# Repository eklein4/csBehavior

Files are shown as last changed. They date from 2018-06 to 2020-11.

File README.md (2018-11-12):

# csBehavior

Tools for running behavioral experiments with Python and Teensy (and related) microcontrollers.

Example Features and Other Capabilities:
State based behavior control.
Runs reliably at 1 KHz.
Visual stimuli and camera tracking via an optional raspberry pi.
Multi-color optical stimulus control.
Event-driven clocking of analog outputs (tying optical stimulus to galvo turnarounds).
Electronic record keeping via mqtt and google sheets.

v1.05 (highly functional and precise, but not totally polished) 
<br>
questions: cdeister@brown.edu
</br>
<br>
contributors: Chris Deister, Sinda Fekir
</br>

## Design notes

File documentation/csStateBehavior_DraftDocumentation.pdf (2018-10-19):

csStateBehavior Documentation (9/22/2018)

About:
“csStateBheavior” is a micro-controller program for running state-based behavioral tasks and/or stimulus delivery.

Dependencies:
csStateBehavior uses some 3rd party libraries. Becuause the program is embedded, you need these libraries to compile and upload the code to a Teensy, even if you aren’t going to use the features they offer. You can install libraries into the Arduino IDE in a variety of ways, but I recommend downloading these libraries, placing them in a .zip and installing them by selecting “Sketch -> Include Library -> Add .zip library”
A) Adafruit’s neopixel library:
https://github.com/adafruit/Adafruit_NeoPixelhttps://github.com/adafruit/Adafruit_NeoPixel/archive/master.zip
This is used to control neopixel strips. Intended use is to have neopixel strips like this: https://www.adafruit.com/product/2847 or any of them, in a behavior rig enabling you to change light colors for cues, habituation reasons, or just to have light around.
B) HX711 ADC Library by Bodge:
https://github.com/bogde/HX711
https://github.com/bogde/HX711/archive/master.zip
This is to interface with and read data from the loadcell. There are a ton of HX711 libraries around, but Bodge got all the “little things” right.
C) Adafruit’s MCP4725 (DAC) Library
https://github.com/adafruit/Adafruit_MCP4725https://github.com/adafruit/Adafruit_MCP4725/archive/master.zip
There are a bunch of MCP libraries around too. This one is fine, and I like Adafruit. This is used to add two more DAC channels via MCP4725 breakouts. I use one from Adafruit and one from Sparkfun, because the default addresses differ. But, you can change the address of either and just buy two from one place. https://www.adafruit.com/product/935

Basics:
By default, csStateBehavior runs at 1 kHz. The program is a state machine instantiated as a function that is timed using and interrupt timer. Each interrupt a function called vStates runs and it:
a) evaluates which state it should be in
b) runs a state header if it enters a new state
c) executes code determined by its state
d) streams, over serial, a data report
e) interacts with experimental devices, with precise timing, via digital, analog, i2c, spi, or UART IO.

It is important to note that the intended approach of the broader csBehavior library to stimulus and behavior control involves using a python program to interact with the teensy, such that real-time processes are effected by the Teensy and the python program saves data, shows plots, and makes determinations about when to change states. In this way, the Teensy program is designed to be as “dumb” as possible, yet it is the core of the behavioral control stack. csStateBehavior provides the master clock, and the state the Teensy is in, is considered by all other interacting processes (like the python program) to be “ground truth.” Programs can request state changes, but the teensy changes the state and provides feedback when it has.

csStateBehavior, by default, sits in “State 0; S0” where it does very little. There is no data report sent in S0. However, in S0, the Teensy does evaluate whether it should move to a new state, responds to serial-based commands, and it can execute a series of pre-programmed device interactions “relays” based on specific relay pins being turned high. These relays are intended to allow other users the ability to gain access to devices attached to your Teensy/Behavior Rig without having to use the program or worry about weird current/voltage states on the dedicated trigger pins. For example, a user may be using Matlab code and NI-

DAQ boards to do their work, but they want to trigger a microscope, change light brightness, and trigger rewards from a pump. Instead of having to split connections, which can lead to unexpected behaviors, the user can trigger a pin on the Teensy and it will do any, or all, of those things. Also, in S0, the state of connected devices can be polled asynchronously for general use. For example, you can change the color of neopixel light strips, play tones, and check the values of attached sensors and devices. Lastly, certain sensors that cannot be polled in real-time can be used in S0 (such as environmental sensors).

Data Report:
What is streamed in the data report changes frequently, and can be customized. As of this writing, the data report streams the following in a serial packet that has a header called “tData:”
a) intCount: this is the actual number of interrupts fired since the Teensy has left S0. By default, csStateBehavior runs a 1kHz, thus, each interrupt is 1 ms. This should be considered to be the actual clock.
b) sesTime: this is the session clock, as determined by evaluating elapsedMillis(). Conceptually, this value should be identical to intCount. It can differ by 1 at the beginning, as sometimes the first ellapsedMillis will report 0 or 1. Beyond that, the two clocks should be identical. If it isn’t, that means the function did not finish evaluating before the next interrupt. Despite common conception, Teensy’s and related boards are very fast, each evaluation of vStates() takes less than 200 us.
c) stateTime: this is the state clock, as determined by evaluating elapsedMillis(), and resetting the reference each time you enter a new state. The intention of this variable is to help make evaluation of state-specific conditions/functions easier. Also, it may help with post-hoc analysis.
d) currentTeensyState (aka knownValues[0]): this is the current state the Teensy is in.
e) loadCellValue (aka knownValues[17]): this is the reading of the loadCell from the HX711 amplifier.
f) lickSensorA_Value: this is the value of the sensor used for determining licks. By default, even digital sensors are treated as analog allowing an external program to threshold as you see fit. csStateBehavior (the hardware) does not evaluate licks in real-time, and does not need to. Though, it is trivial to configure csStateBehavior to do hardware lick detection.
g) encoderAngle: this is the value reported by a rotary encoder used to track the location of a wheel.
h) pulseCountA: this is the incremental pulse count determined by an interrupt-based pulse counter. It can be used to keep track of elapsed frames from a two-photon microscope or ccd camera, etc. It resets every session.
i) loopTime: this is the amount of time in micro-seconds that the function took to evaluate for the last interrupt. The default clock rate of csStateBehavior is 1kHz, meaning that the interrupt timing the state machine function fires every ms, no exception. However, if the function does not return within a ms, you will fail to log those interrupts. Loop time allows you to identify problematic interrupts and fix any issue that may be slowing down the program. As configured, each loop of the main function takes 500-720 microseconds, depending on details of how it was compiled, primarily.

j-m) genAnalogInput0-3: these are the values of 4 different analog inputs chosen by the user. Just add your device to these and it will record the value. Note that the teensy is an arm-based computer and operates at 3.3V, the analog input has to be between 0 and 3.3V, not only to be precise, but the pins will become damaged if you drive them above 3.3V. Use a voltage divider to scale the peak voltage to 3.3V if you have something you know to exceed that voltage.

Generic State:
The generic state consists of the following:
A) State Header: code that only runs when you enter the state.
B) State Body: code that loops until you leave the state.

Every state runs the default state header and body. You can override these, and you can supplement them (prefered).

Anatomy of the default header:
The concept of “the header” is code you want to run only once and specifically when you arrive to the state. The obvious use of this is to reset a timer. Here is what the default header looks like:

void genericHeader(int stateNum) {
// a: reset header timer
headerTime = 0;
// b: reset header states and set current state's header to 1 (fired). resetHeaders();
headerStates[stateNum] = 1;
// c: set analog output values to 0.
analogOutVals[0] = 0;
analogOutVals[1] = 0;
analogOutVals[2] = 0;
analogOutVals[3] = 0;
// d: reset state timer.
stateTime = 0;
}

What this does is to reset a header timer, resets the state of all other state’s headers to 0 (hasn’t fired) while also setting the current state’s header to 1 (has fired), then it zeros out the analog output voltages ensuring that if you entered the state in the middle of a stimulus, it doesn’t hang, and lastly it resets the state timer.

The concept of the state timer (stateTime) is most important in creating your own states. Typically, you will want to do things based on how long you have been in a state. You can program hardware specific logic, but I recommend using the python component to react to time events etc. I mention this here because this variable (stateTime) is streamed over to python.

Anatomy of the default state body:

void genericStateBody() {
lickSensorAValue = analogRead(lickPinA); lickSensorAValue = analogRead(lickPinB); genAnalogInput0 = analogRead(genA0); genAnalogInput1 = analogRead(genA1); genAnalogInput2 = analogRead(genA2); genAnalogInput3 = analogRead(genA3); analogAngle = analogRead(analogMotion); writeAnalogOutValues(analogOutVals);
If (scale.is_ready()) {
scaleVal = scale.get_units() * 22000;
// this scale factor gives hundreths of a gram as the least significant int knownValues[14] = scaleVal;
}
}
What this does is, reads the values of up to two connected lick/touch sensors, the four generic analog inputs, an analog encoder, writes the currently desired/computed analog out voltages (see below) on the analog output channels, then it looks to see if load cell data is available, if so it grabs it and scales it to give useable numbers.

You can add specific code to the header or body in your custom state. Here is an example state:

// ************************** // State 1: Boot/Init State // **************************
if (knownValues[0] == 1) {

if (headerStates[1] == 0) { visStim(0);
genericHeader(1);
blockStateChange = 0;
}
genericStateBody();
}

From the top, this state is entered if the state variable (knownValues[0]) is 1. If it enters the first time (as indicated by it’s header bit being 0) it will zero out a visual stimulus (added code), run the default header, and will allow python to control the state (blockStateChange = 0). After this, the header bit will be set to 1 (which happens in the default header) then, it can’t run anymore as long as the program is stuck in state 1. But, instead, it will always fire “genericStateBody()” that is the default state body. If I wanted to add some code that changed the state after 100 ms, I could add the following:

// ************************** // State 1: Boot/Init State // **************************
if (knownValues[0] == 1) {

if (headerStates[1] == 0) { visStim(0);
genericHeader(1);
blockStateChange = 0;
}
genericStateBody();
if (stateTime >= 100){
// note that stateTime is in milliseconds knownValues[0] = 2;
// send teensy to state 2
}
}

But, as you will see in later parts of the documentation, it is recommended you handle such things in python. However, the more event logic you program on the teensy, the more close to true real-time performance you will get. The above code will move the teensy to state 2, in real-time, once 100 ms has elapsed, but if you are coordinating with the python component, it will need to be made aware.

There are two basic approaches to two components interacting dynamically, one is to have all events on the hardware, and stream the data for logging in software. Or, one can have the software log data, and determine state flow. The csBehavior library biases things towards software control in order to take advantage of richer computation and to allow maximal flexibility.

Analog Output:

Each sample’s analog output value is kept in an array called “analogOutVals.” By default, the generic state header, which every state executes, writes all DAC values to 0. analogOutVals is isolated from the array pulseTrainVars, which keeps track of all variables needed to generate waveforms. Thus, overriding the output value is non-destructive. If this doesn’t seem important to you right now, that is ok there will be more on why this is important later. What matters for now is that pulseTrainVars and analogOutVals work with each other.

When you enter a state, the generic header will set the analogOutVals to 0. If you want to write a simple DC value on the DAC lines you can, even in the header. Each state’s header allows for custom header code, that is executed after the genetic header. Thus, if you want two channels to be 3.3V for the whole state, you can set analogOutVals[0] = 4095; and analogOutVals[1] = 4095; in your header code. The reason we write the values to 0 by default is so the devices don’t hang and so you can start fresh each state. Another benefit is that if you don’t use analog out for a state, or at all, you don’t have to do anything because the DAC lines will all write 0.

If you want controlled output in a state the generic pattern is to execute the following helper functions in the body:

stimGen(pulseTrainVars);
setAnalogOutValues(analogOutVals,pulseTrainVars);
writeAnalogOutValues(analogOutVals);

What these do is first, “stimGen” use all the variables in pulseTrainVars (explained later) to determine what value the channel should have based on a desired waveform and the current time. Second, “setAnalogOutValues” simply writes the calculated value from stimGen (stored in the pulseTrainVar array) as the analogOutVal. Lastly, “writeAnalogOutValues” writes the analogOutVals to the DACs.

These functions just homogenize a bunch of somewhat heterogeneous code. For example, csStateBehavior supports four true 12-bit analog outputs, two of which are native to the Teensy3.5/3.6 and two are added with MCP i2c analog out boards. The writes to these channels are slightly different.

Now, we place writeAnalogOutValues in the generic state body. So, you just have to add stimGen and setAnalogOutValues to any state you want to use analog output on.

Here is example code for a simple analog output state (State 7 in the default code):

// ****************************************
// State 7: Single Pulse Train Trial State
// ****************************************
else if (knownValues[0] == 7) {
if (headerStates[7] == 0) { genericHeader(7);
visStim(0);
blockStateChange = 0;
}
stimGen(pulseTrainVars);
setAnalogOutValues(analogOutVals,pulseTrainVars);
genericStateBody();
}

You can set key parameters that determine the waveforms that go over the analog out lines over serial. On every interrupt the function “setPulseTrainVars” is called and it will register any changes commanded over serial. The actual processing of a variable change takes 18 microseconds, but the latency of variable changes will be determined by how fast the serial command gets to the Teensy. When using the csBehavior.py python program, the latency is typically 1-10 ms. This is more than adequate to drive variable stimulus trials. However, if you need more real-time performance I suggest programming logic in your state that responds to inputs and makes local pulse train variable changes. Under those conditions, you can change pulse train variables with sub-millisecond latency. Below I describe the setPulseTrainVars function and document the serial codes needed to change pulse train variables.

On every interrupt, the program looks for new variables over serial. These variables control a variety of things. The pulse train variables work a bit differently than the rest. Because there are up to four DAC channels, each variable needs to have a value and a target channel.

setPulseTrainVars(curSerVar, knownValues[curSerVar]);

The variables are as follows:
d: interpulse interval in milliseconds.
p: pulse duration in milliseconds.
v: amplitude of pulses in raw 12-bit value with 0V = 0 and 3.3V = 4095
t: stimulus type (0 for square waves; 1 for ramps; more to come).
m: max pulses/ramps to do in a state (optional: you can use this to limit the number of pulses)

The way you call each variable is to send the variable header letter above, followed by an integer value, then followed with an integer channel (1-4), and lastly the character ‘>’ send as one line.

As an example, to make the pulse duration of channel 2 80 ms, we send:
‘p802>’

The program knows the ones position is the channel and the rest is the value to use. The intention behind the design is that if you want to do some standard experiment where you drive an analog device like and LED etc. on a trial-by-trial basis, you can make a stimulus sate (csStateBehavior’s default state 7 is an example of this) and toggle between a wait state (such as state 1) and the stimulus state. In this scenario you can set the current trial’s stimulus variables in state 1 while you wait for some event to occur, like a baseline period to elapse, and then transition to state 7, where your stimulus will start. Using the python program csBehavior.py you could determine a trial’s stimulus amplitude based on randomizing a range, or some other criteria, then in state 1’s header you could push the variables and then once some baseline condition is met python can tell Teensy to move to state 7 and stimulate.

Using the “max pulses” variable you can limit the number of pulses delivered in a manner that is independent of time. For example, if you wanted to deliver 10 pulses of an LED, on channel 1, at 10 Hz, but have a two minute post-stim period, you could pass m101> and d1001>, then in your stimulus state you can track channel 1’s max pulse counter, which is in the array pulseTrainVars which is a 4x9 array that has all the DAC values. pulseTrainVars[0:3][8] is the max pulse tracker. It decrements every time a pulse or is completed, until it gets to zero. So, you could have the following logic in your state:

If (pulseTrainVars[1][8]==0){
pulseTrainVars[1][5] = 0;
}

pulseTrainVars[1][5] happens to be channel 1’s amplitude.

It may now be helpful to document pulseTrainVars organization:

At compile time it is initialized in the following way:

uint32_t pulseTrainVars[][9] =
{ {1, 1, knownValues[9], knownValues[10], 0, knownValues[11], knownValues[12], 0, 0}, {1, 1, knownValues[9], knownValues[10], 0, knownValues[11], knownValues[12], 0, 0}, {1, 1, knownValues[9], knownValues[10], 0, knownValues[11], knownValues[12], 0, 0}, {1, 1, knownValues[9], knownValues[10], 0, knownValues[11], knownValues[12], 0, 0} };

Ugh :(

Not too worry. That code is specific to the way things are handled internally. What is important is position along a row, each row is a DAC channel. Arrays are zero indexed.

0: pulsing or waiting: this is a state variable that is used by the pulse generator to keep track of whether the channel is pulsing or baselining.

1: sample counter. This is used to keep time in the train.

2: interpulse interval duration in ms, this is the variable you can set with ‘d’ over serial. You can set it locally by writing to pulseTrainVars[chan][2]

3: pulse duration

4: baseline amplitude (defaults to 0).

5: pulse amplitude, encoded in raw 12-bit format Teensy 3.6 is 3.3V so 0 is 0V and 4095 is 3.3V and all in between.

6: stim type, 0 is square waves and 1 is ramps

7: write value, this is the calculated valued based on waveform parameters to write on that sample.

8: max pulse counter, this is a counter that decrements to zero, and can be used for control purposes.

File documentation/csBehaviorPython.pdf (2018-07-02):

csVisual Documentation - v0.3 Chris Deister - 1/28/2018
cdeister@brown.edu
0) Introduction
csVisual is a group of tools used to implement behavioral tasks and experiments that involve the delivery of timed visual stimuli. The backbone is a program that runs on a Teensy micro-controller (PJRC.com) and a Python 3 program. csVisual is ‘state-based’ and the specific states active at any moment are active across all hardware and software components. The states follow a basic generic structure that allow for relatively rapid configuration and customization in order to implement different types of tasks and experiments. In order to introduce you to the basics, we will work through a very stripped down version of the Teensy script and build it up in order to implement a visual detection task.
1) Example: Implementing a Detection Task
The state diagram for our detection task is to
the right. Here, we start with a boot/init state we call S0. S0 is the state we expect to find the Teensy in every time we connect to it with any other program. In S0, the Teensy will not track time or stream data to its recipient. Also, S0 is a convenient place to poll for new variables that we will use through a trail. Once we establish a connection and change variables etc., we move on to the rest of the trial. We want our subjects to start each trial in as close to the same “behavioral state” as possible. What I mean by behavioral state is that the animal is not moving around appreciably, attempting to lick for a reward, and maybe less obvious things like the eyes aren’t moving around too much. In the state diagram to the right, I denote these behavioral state conditions being met as “still,” just to be short about it.

Once the animal is still, either a stimulus trial, or a catch-trial without a stimulus is offered after some variable period of time. If we selected a stimulus trial, we move the subject to S2, where a visual stimulus will be triggered and we will monitor licking at a spout. If the animal licks at the right time, in a manner consistent with its training indicating it perceived the stimulus, then it will be rewarded in S4 with water at the spout, otherwise it will move on to the next trial. If we selected a catch-trial, we move the subject to S3, where no stimulus will be presented. In S3 we will also monitor licking, if the animal licks as
if to report perception we send the animal to a
punishing time-out state (S5).

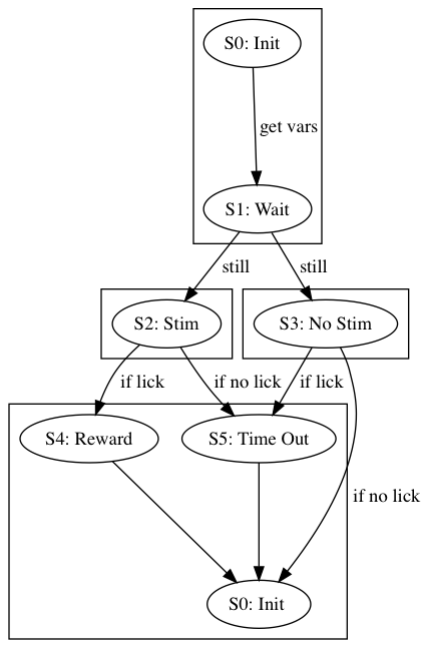
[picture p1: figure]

What I hope is clear is that in each state we more or less do the same thing. We need to keep track of time (true about any experiment), we also need to poll external variables and make decisions about when to move to a new state, or when to stay put. In addition, we need variables to be polled to tell us what to do with specific things in specific states. For example, in S1 we need to make sure the lick rate of the subject is at 0 for some specified period of time, as well as its motion is at 0 etc. In order to

- 1 of 4 -maximize training, we may even want the tolerance for errant licking etc. to be wide early in training and converge to a more conservative cut-off as the subject progresses.

We start with the Teensy program and flesh out the basic core state. For reference, I will be describing a script called “csVisual_Detection” in the GitHub repository. I expect you are using a Teensy 3.6 controller, but there is critical reason for this. Frankly any microcontroller will work. What I like about Teensy boards are their size, power, and number of hardware serial lines. Moreover, Paul at PJRC maintains robust libraries that are very useful. Unlike a typical Arduino/Teensy program I do not use the main loop to run our task. Instead, we will use an interrupt timer to time calls to a task function that will behave like our main loop would. We call this by including “FlexiTimer2” (https://www.pjrc.com/teensy/td_libs_MsTimer2.html) (https://www.pjrc.com/teensy/td_libs_MsTimer2.html) in our program and then scheduling the timer in the setup block:

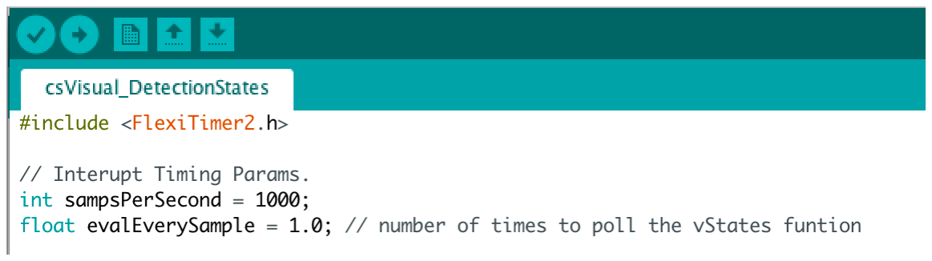
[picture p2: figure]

After the include statement, I specify two variables necessary for flexiTimer. ‘sampsPerSecond’ sets the sample rate and ‘evalEverySample’ sets how often the interrupt will poll the function. We want it to poll every tick of the interrupt and that will occur once every thousandth of a second.

We then start the timer in the setup block (see highlighted lines):

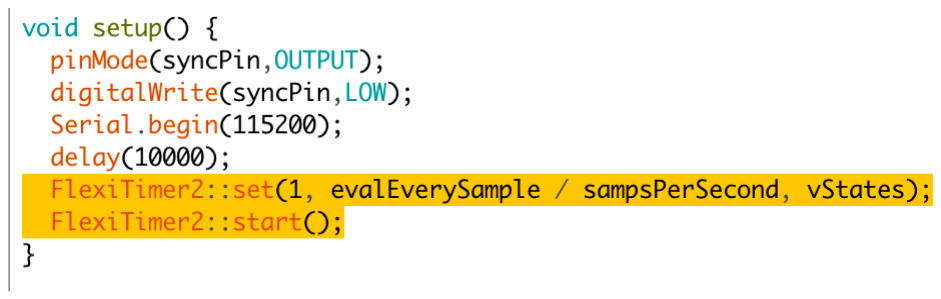
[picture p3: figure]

The reason I mention this is because you may not be familiar with this interrupt style of programming. The reason for it, is to ensure we have a reliable clock. We are going to treat this Teensy as the ‘master’ of our data-acquisition (DAQ) chain.

Note our loop block is blank, but our ‘vStates’ block is lengthy (and there are many other functions):

- 2 of 4 -

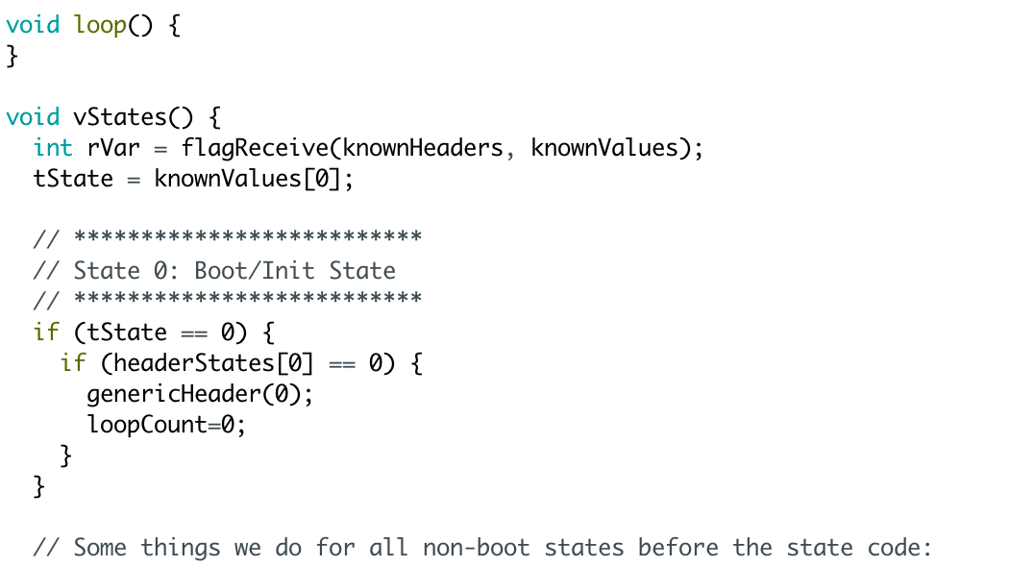
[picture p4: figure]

With that out of the way there are two main ‘types’ of states. One, is the “boot state,” which we will call State 0/S0. All other states are “Non-Boot States.”

Let’s look at S0:

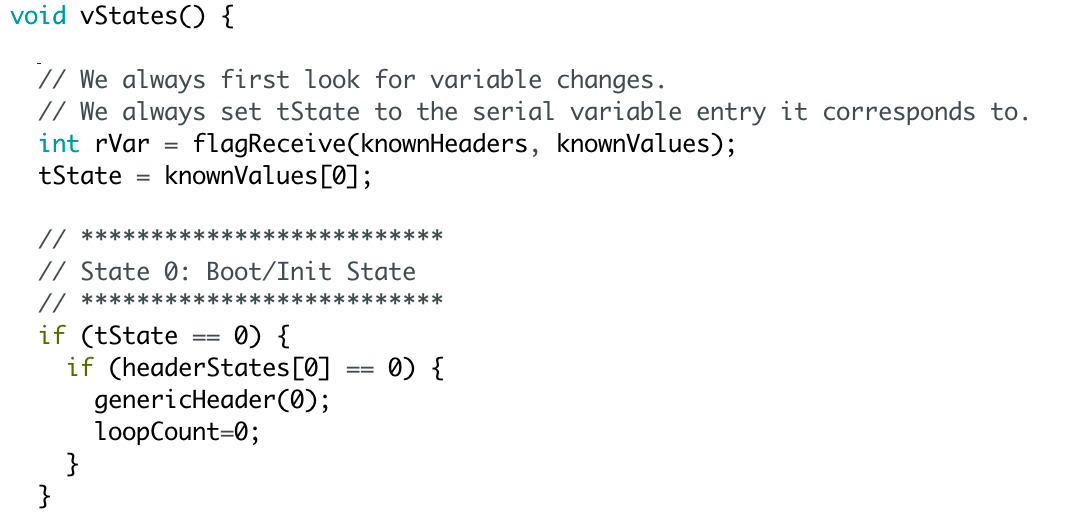
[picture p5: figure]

On every iteration of vStates, we execute two lines, even before we execute any S0-specific code. We look for any variables that have been sent from the Python program (more on that later) using ‘flagReceive,’ which will be explained later. tState is then set. The ‘knownValues[0]’ value will become clearer later, but it is part of an array that tracks variables that can be set over serial. Python controls the states and the Teensy is to follow along. Because tState is polled every sample and before we look for which state’s code gets executed, we can change state every sample.

We initialize knownValues[0] to 0, so the Teensy will start in 0, but when you change trials or quit the Python program, you will need to set the Teensy back to 0. I will explain how to do that later.

Every state has the following structure:

> Header: Code executed once on entry. Useful for resetting counters etc. * We execute a generic header, which resets a timer offset for tracking state time.
* In the generic header we also set the headerState for state 0 to
1 and all others to 0.

> Body: State 0 is missing the body, but for all other states we track total time and state time, at a minimum. But, this is where we would insert code for monitoring state and sensors. Also, data is relayed back to the Python program for parsing, plotting and saving.

> Exit: From the Teensy side, we would rarely implement this, because we want the Python program to be in control.

We add custom code in S0 header to reset ‘loopCount,’ this is used to track how many interrupts we’ve ticked through the whole trial, and ensure the number of interrupts matches up with our time stamps.

Next we will look at the more standard states:

- 3 of 4 -

I end here — 1/28 … will continue later. Check the code for now :)

- 4 of 4 -

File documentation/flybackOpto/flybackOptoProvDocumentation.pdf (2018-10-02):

Flyback Opto Stim: 10/01/2018

Chris Deister
cdeister@brown.edu

Problem:
When using photomultiplier tubes (PMTs) to detect fluorescence, as is done with standard two-photon laser scanning microscopy (2P), it is unwise and/or scientifically problematic to turn on light sources that emit in the range the detectors are tuned to. The specific reason for this technical note is to address and document a way to minimize light contamination of 2P imaging data from blue, red, green and orange LEDs used for many optogenetic experiments. Jakob Voigts and I used this in the course of experiments we did for his graduate work on the functions of layer 6 neurons. We got the idea from Winfred Denk’s retina papers, where his group has needed to activate the retina with UV light while also conducting 2P imaging.

Approach:
What the Denk group does is to use the short period of time in between scanned lines where the y-galvonometer moves the 2P excitation beam to its next line. This is often referred to as the “flyback.” The flyback is short at ~10-50 microseconds, but it occurs at relatively high rates. For resonant scanning, the repetition rate between lines (including the flyback itself) is 64 microseconds. For galvo-galvo scanning, with typical dwell times, the time between lines is slower at about 600-800 microseconds, again including the flyback itself. In either case, the repetition rate of flyback is fast enough for us to use the time between flybacks as a clock with which we can time the optogenetic stimuli. However, the “trick” relies on more than just the flyback occurrences as a clock. Nevertheless, that concept is the baseline, and the “sample rate” our flyback clock affords us is 1-15KS/s. Thus, factoring in Nyquist, we should be able to generate pulse trains with frequencies in the range of 500 Hz - 7 KHz — plenty for most optogenetic experiments that typically use 1-50 Hz.

Sampling with end of line triggers
As mentioned just using the onset of a flyback as our clock isn’t the whole story. Because the flyback time is 10-50 microseconds, we are afforded enough time to gate a light source, assuming we can turn it on and off on the timescale of 10 microseconds or so. Some diode lasers can be modulated on the KHz timescales, which may be sufficient in some cases, but in general these lasers are expensive. An acousto-optic modulator can conceptually gate even a poor laser at sufficient speeds. But, solid-state LEDs are ideal. The LEDs used in most labs for optogenetic stimuli are driven by current source driver circuits that are poor overall, and impossible to use for our purposes. But, the LED itself can be gated at arbitrarily high rates. This is not the place to complain about “buck-type” LED drivers, and others can do that better. But, most fiber-coupled LEDs operate when driven by 300-1000 mA of constant current. Buck drivers can provide a constant current source, but they have a variety of capacitors and coils in them which ultimately lead to a slight exponential rise and decay to their steady-emission state when turned on. The time constant of this rise is hundreds of microseconds, thus finite predictable light pulses of 10 microsecond duration are hard (impossible) to achieve with buck drivers. You can just gate the LEDs with beefy mosfets, but then it becomes tricky to change current levels on the fly (dimming). I recommend Jon Newman’s amazing “Cyclops” LED driver, which is an open source driver that provides all the upsides of mosfets, but is purpose built for optogenetic experiments and fluorescence imaging.

https://github.com/jonnew/cyclops
https://www.open-ephys.org/store/cyclops-led-driver

Use of mosfets or the Cyclops allows us to assume that even if we trigger the driver for 10 microseconds it will turn on, emit, and turn off all within that period of time. Thus, if you have a 20 microsecond flyback, as long as we can take a signal signifying the end of a line and turn it into a trigger, we can turn an LED on only during the flyback.

PMT blanking and PMT decay
We have established that we can use the onset of flybacks as a sample clock for drawing optogenetic stimulus waveforms, and we have established that LEDs can be gated at the speeds needed to “inject” photons in a narrow period of time where we aren’t saving imaging data. We aren’t done though. In most systems the PMT stays on during the flyback, its just that the data isn’t saved. In some cases the Pockels Cell is blanked during the flyback (as in resonant scanning), but the PMT remains on. There is good reason for this as PMTs do not turn on instantly, instead, they take microseconds to reach their steady state in both sensitivity and decay. Meaning that if we were to apply some voltage to a PMT and deposit a few photons onto it for 1 nS, and then watch what happens over the next 100 microseconds, we would see the PMT takes 10 microseconds or so to fully decay back to 0. Likewise, if we leave a PMT off for 100 years, then turn it on for that 1 nS where we place 10 photons onto it the value the PMT will tell us is a fraction of what it would tell us if we waited a hundred microseconds or so. This means that we need to rapidly turn the PMT off during the flyback, inject some photons, turn it back on and wait a bit before we scan the next line. All of this is possible, but requires some electronics and programming.

I want to say at the outset that no matter what we do, turning the PMT off and back on leads to settling time that we can not fully work around. We found that some small proportion of each line, where a light was gated in the flyback, shows signs of signal stabilization (usually dimmer that it would be).

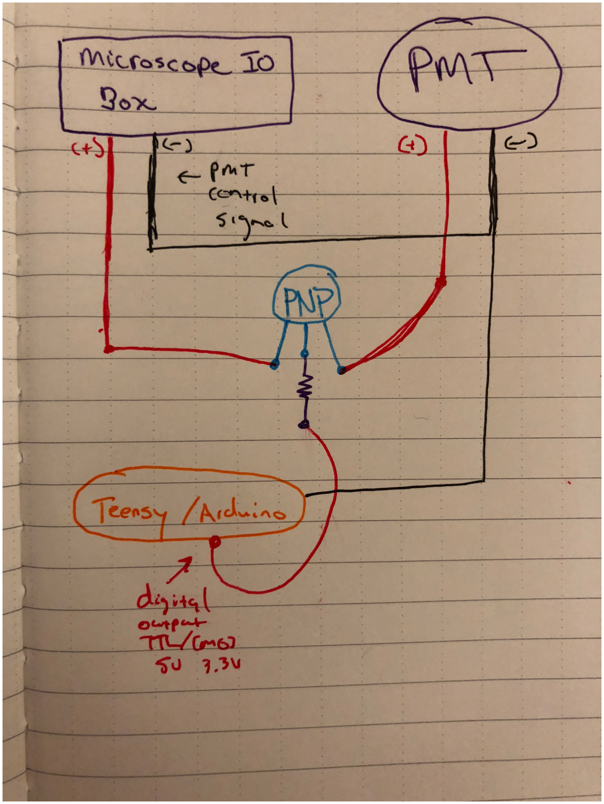
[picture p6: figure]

To rapidly “blank” a PMT, the control signal
to it needs to be gated by a PNP transistor
(normally on transistor). When you vary the PMT sensitivity in your microscope software, you are regulating the voltage on the PMTs. This control signal is an analog signal that is likely 0-5V. A PNP transistor allows the control signal to be on like normal, but you can send a TTL/CMOS pulse to turn the control signal off. In this case, your system will work like normal, unless you send a signal to intervene. For most people, controlling up to two PMTs is typical (green and red). To the right is an example circuit using basic and cheap MPS2907A PNP transistors:

https://cdn-shop.adafruit.com/product-files/2975/MPS2907A-D.PDF (https://cdn-shop.adafruit.com/product-files/2975/MPS2907A-D.PDF)

These transistors are “high load,” which means they can gate 800 mA of current. That is PLENTY the control signal to the PMT, which is a buffered control voltage and has 10-20 mA, at most.

Here is an actual prototype for 2 channel control:

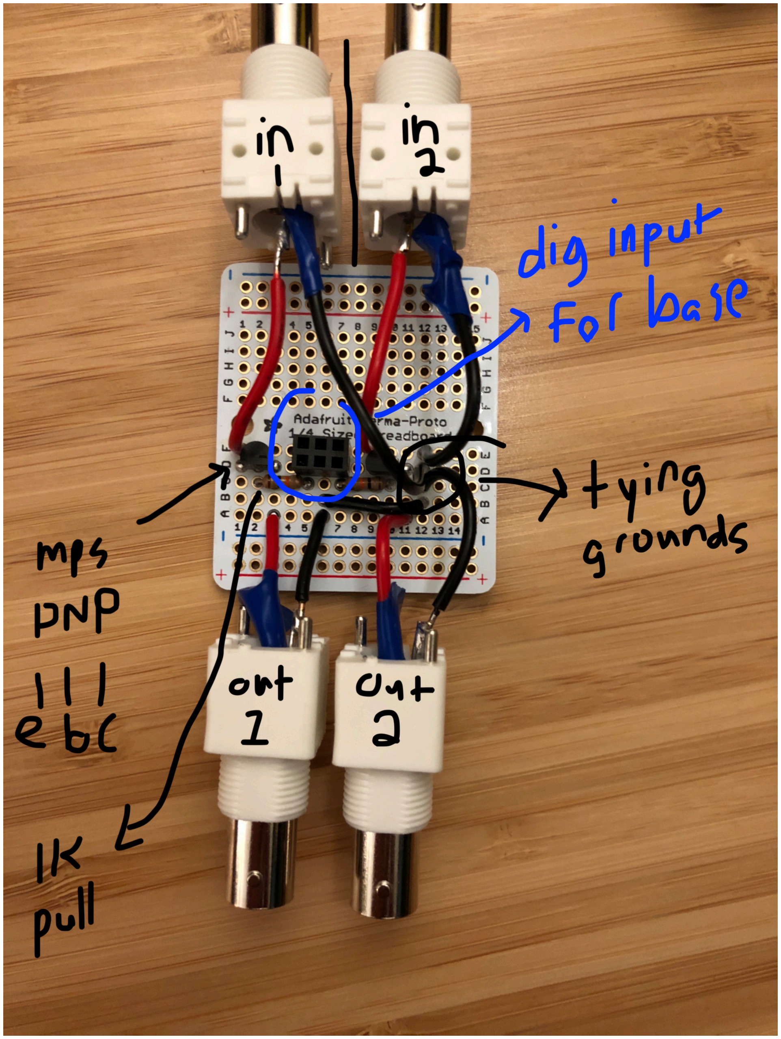
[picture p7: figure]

For this, the orientation of the PNP is emitter-base-collector (ebc), from left to right, respectively. The input’s signal provided by its BNC is connected to the emitter and the routed our of the transistors collector unless the base is pulled high. The base is connected to any digital pin on a teensy/arduino via a 1-10K pull up resistor. Note, I soldered in a 2x3 female pin receptical such that the pull-up is on the same column (#1 and #3) and the middle row is connected to ground. This allows you to easily plug in a wire from an arduino/teensy that is gate, ground, gate.

A teensy/arduino can be programmed to respond to a trigger indicating the onset of a flyback and turn the PMT off using the above circuit. At the same time, the teensy can gate the Cyclops driver, and then the PMT back on.

I’ve added these routines into “csStateBehavior” and they are triggered by a digital input on a Teensy 3.5/6’s pin 35 (by default), set as an interrupt. Thus, in any state, at any time, an input on 35 will blank the PMTs, and determine what voltage to send to a Cyclops led driver, based on a desired pulse waveform (also handled by the teensy.)

Here is the routine (just for conversation purposes; details aren’t crazy important):

void flybackStim() {
elapsedMicros pfTime;
pfTime = 0;
digitalWrite(PMTPin,HIGH);
while (pfTime <= knownValues[15]) { stimGen(pulseTrainVars);
analogWrite(DAC1, pulseTrainVars[0][7]); analogWrite(DAC2, pulseTrainVars[1][7]); }
analogWrite(DAC1, 0);
analogWrite(DAC2, 0);
digitalWrite(PMTPin,LOW);
}

What it does is it a) starts a microsecond timer called pfTime, b) resets the timer, c) sets the PMT base high (to blank the PMT), d) uses the stimGen routine to determine what DAC values should be written based on your desired variables, then writes the values on the DACs, e) when the timer is greater than the desired flyback duration (stored in knownValues[15]) it returns, f) then sets the DACs to 0, and turns the base off (allowing the PMT to come back on).

The details about analog outputs and how to vary them is in the main csStateBehavior documentation.

This function is attached to a trigger pin as an interrupt. How we generate a TTL to signal a flyback is our last remaining detail.

Signaling/Predicting/Detecting Flybacks:
(Will finish 10/3/2018)

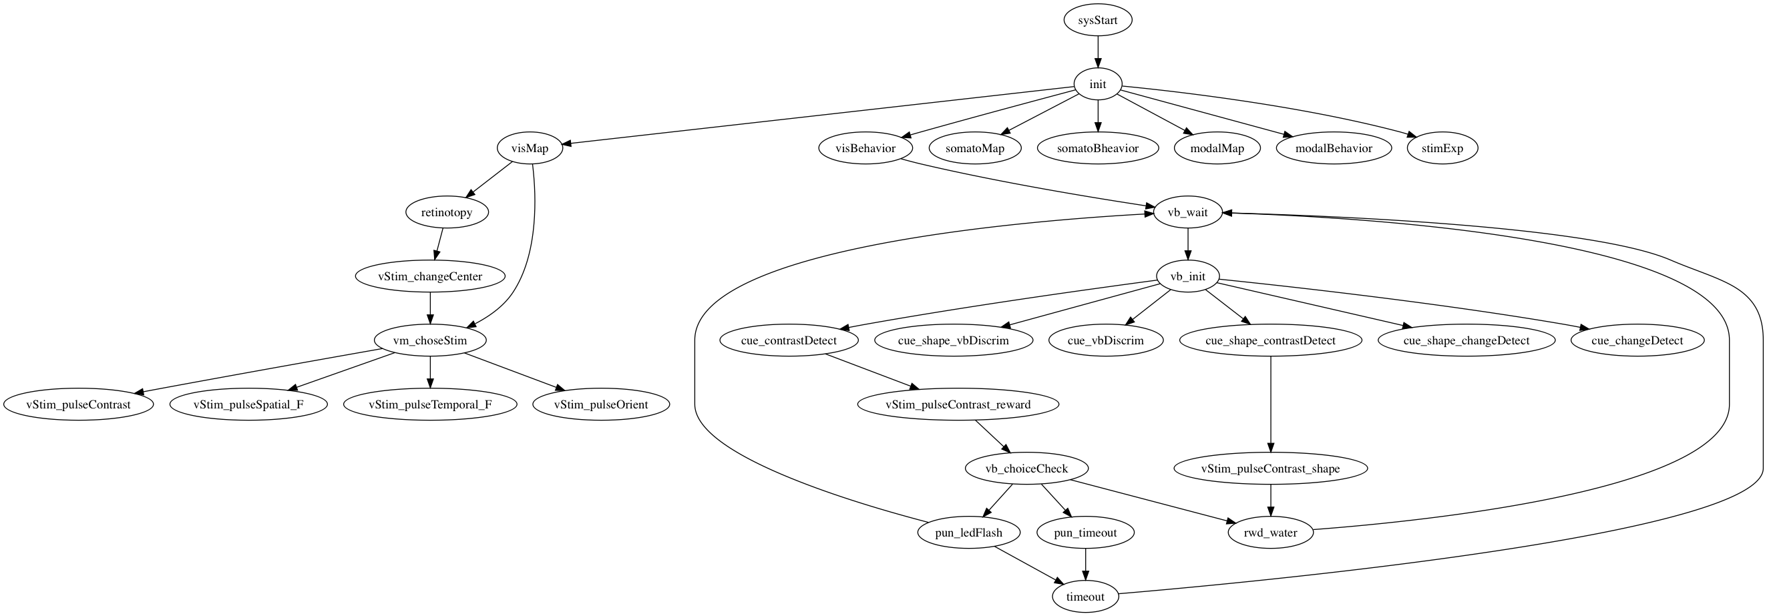
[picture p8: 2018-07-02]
documentation/baseFiles/stateGraphs/discrimStates.png

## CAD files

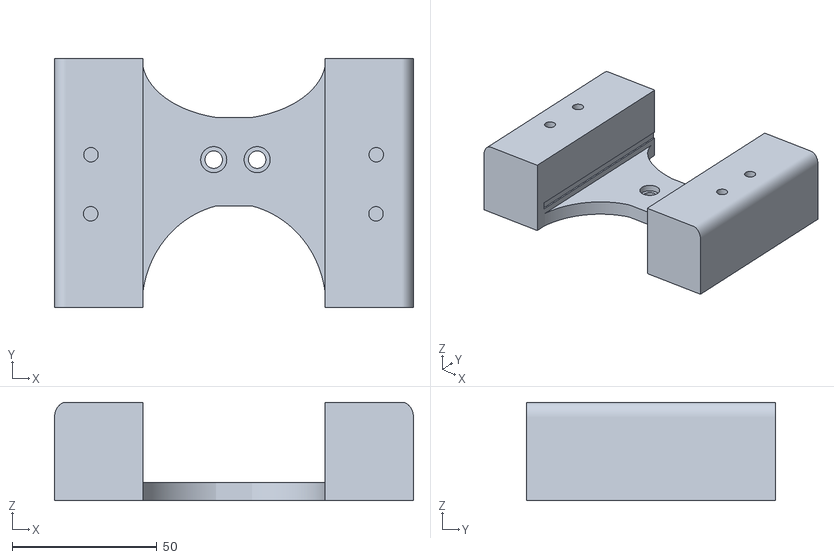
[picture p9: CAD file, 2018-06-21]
RigParts/mouseWheel/mainMount.stl
124.0 x 86.1 x 34.0

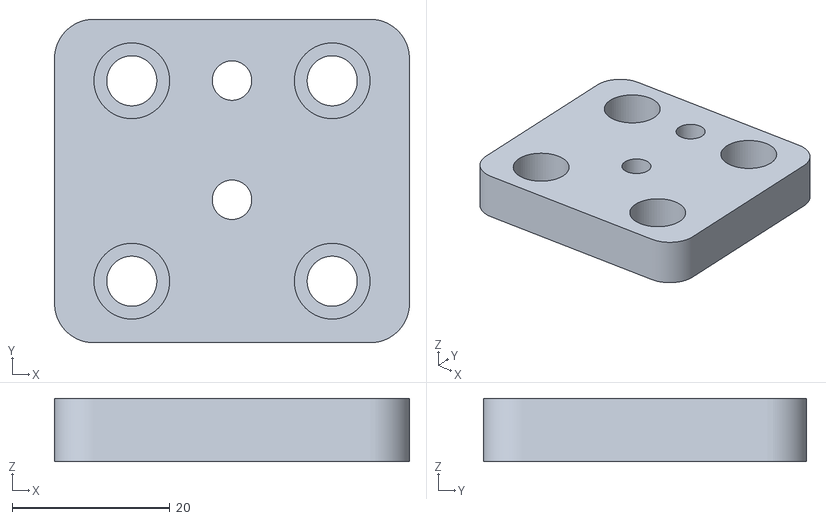
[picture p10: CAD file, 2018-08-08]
rigParts/loadCellAdapterMain.stl
45.0 x 41.0 x 8.00

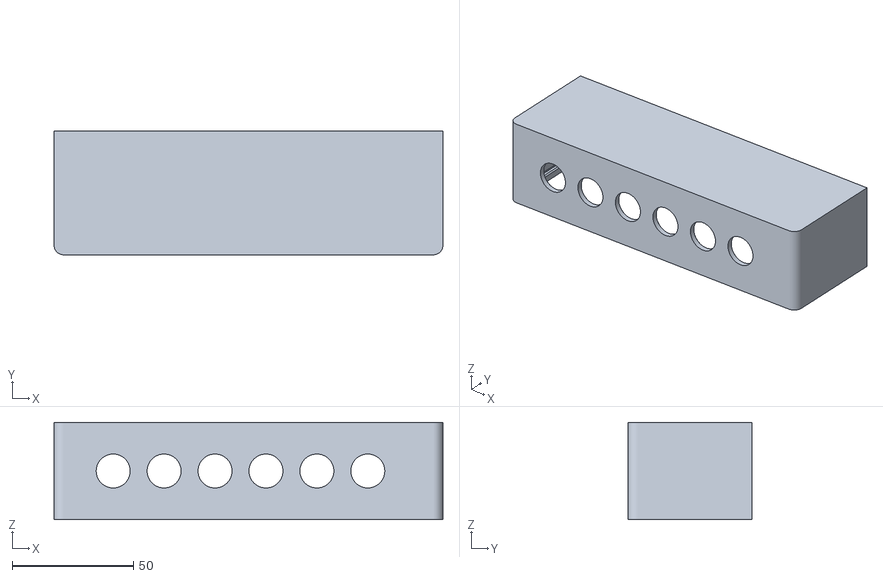
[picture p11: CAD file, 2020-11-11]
rigParts/moreDACBox.stl
160.4 x 51.0 x 40.0

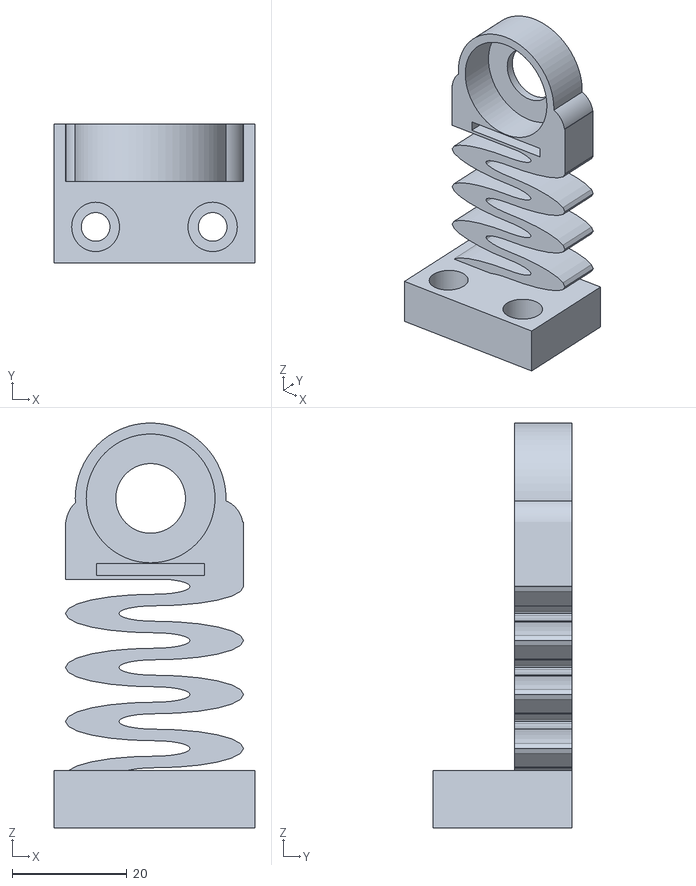
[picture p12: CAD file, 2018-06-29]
RigParts/mouseWheel/bearingWSlot.stl
35.0 x 24.2 x 70.6

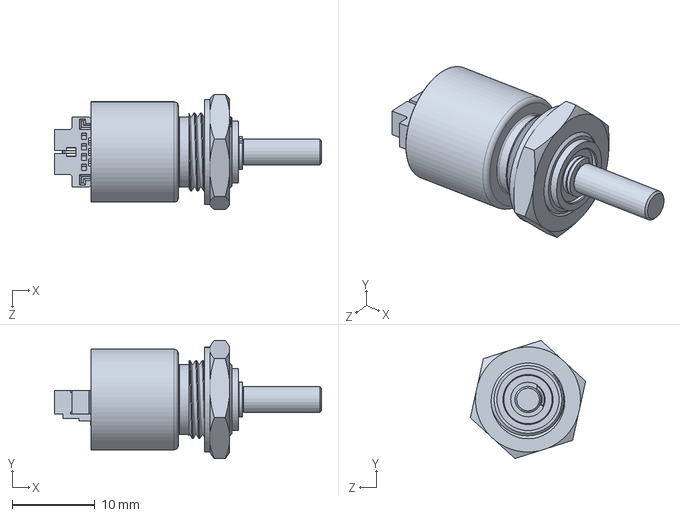
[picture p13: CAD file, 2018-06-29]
RigParts/mouseWheel/helpfulModels/MA3-X-125-B.SLDPRT
32.4 x 14.3 x 14.0 mm

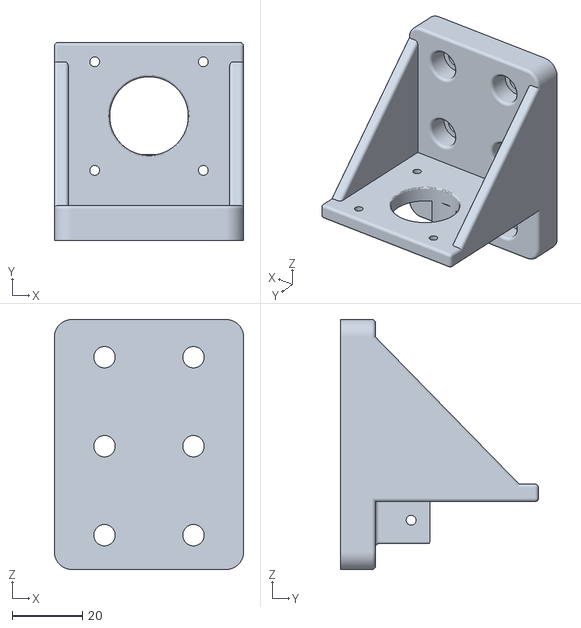
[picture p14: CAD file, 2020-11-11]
rigParts/pump/sp_nema2.stl
54.0 x 56.5 x 71.4

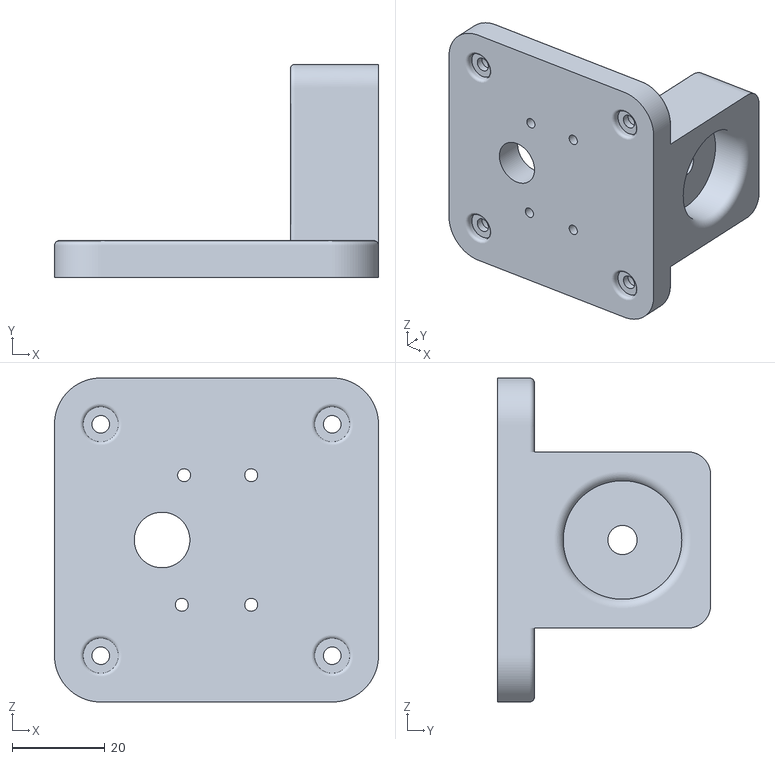
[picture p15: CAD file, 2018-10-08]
rigParts/screen/mangaScreenPostMount.stl
70.0 x 46.1 x 70.0

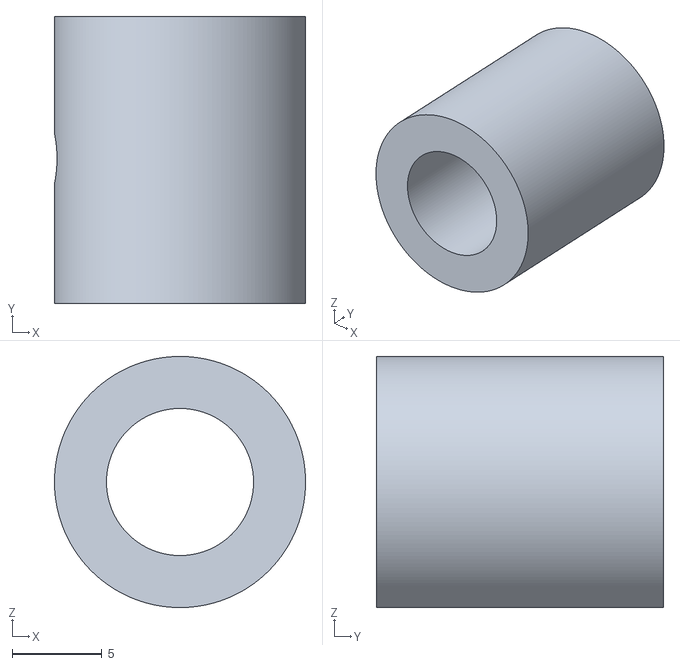
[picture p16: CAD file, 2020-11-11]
rigParts/collet.stl
14.0 x 16.0 x 14.0

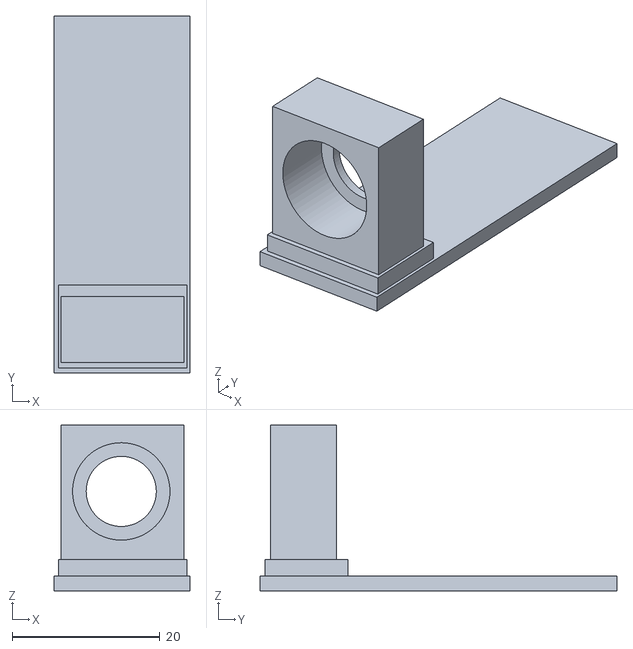
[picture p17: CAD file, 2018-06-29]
RigParts/mouseWheel/encoderMountV0.stl
18.4 x 48.4 x 22.5

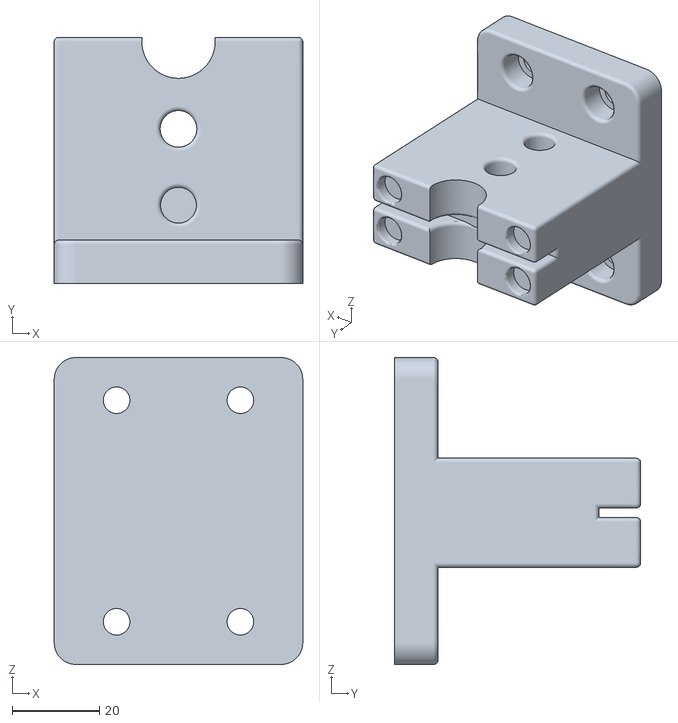
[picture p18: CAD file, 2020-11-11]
rigParts/pump/endCapSyringe.stl
57.0 x 56.5 x 70.4

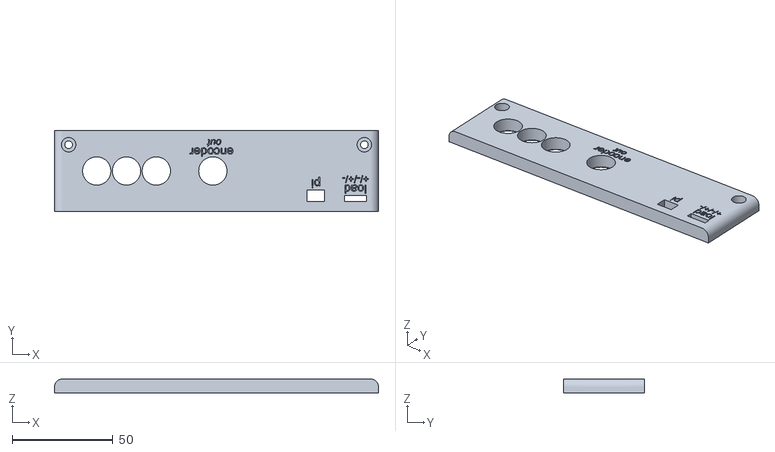
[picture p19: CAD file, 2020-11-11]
rigParts/dacBoxF.stl
160.4 x 40.0 x 7.00

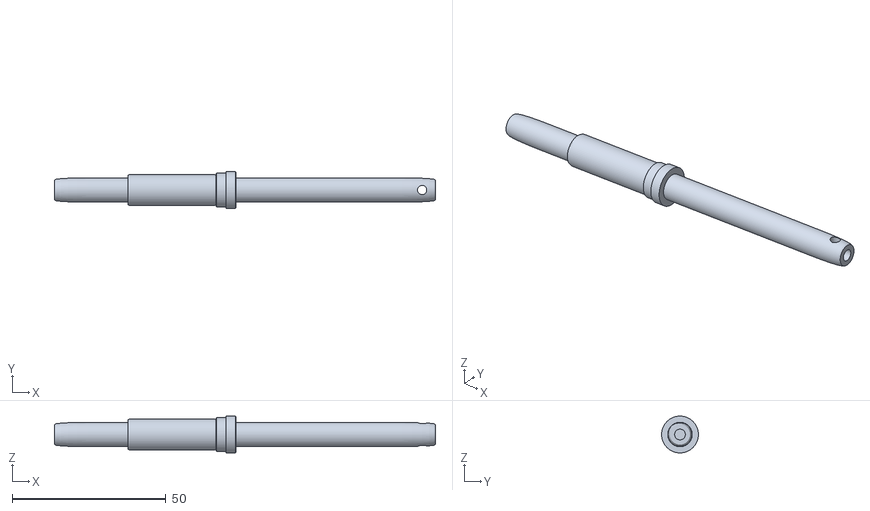
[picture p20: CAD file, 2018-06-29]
RigParts/mouseWheel/rodWheelV2.stl
124.0 x 12.0 x 12.0

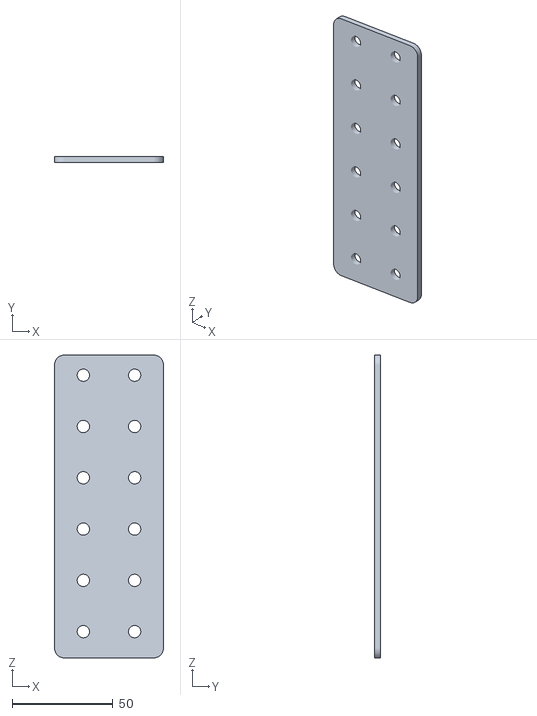
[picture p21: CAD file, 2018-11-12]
rigParts/pump/sp_sixInchBase.stl
54.0 x 3.00 x 150.0

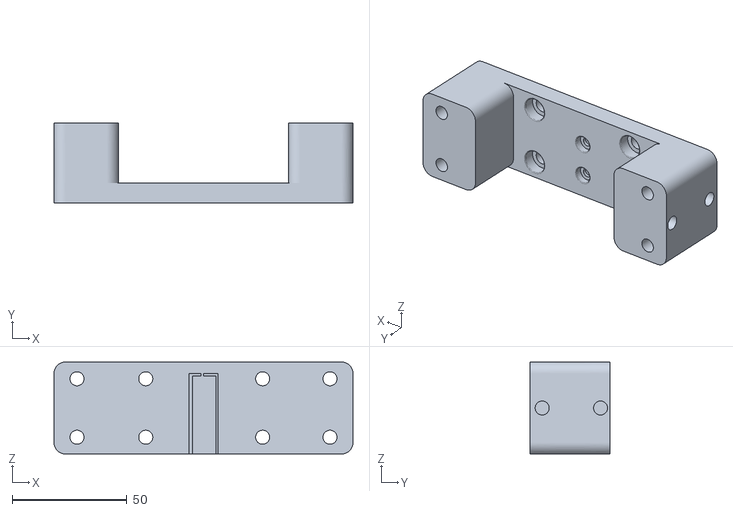
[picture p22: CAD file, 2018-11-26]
rigParts/flexMount2v4.stl
130.0 x 34.6 x 40.0

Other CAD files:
rigParts/pump/alt_sp_nema17Mount.stl
RigParts/mouseWheel/wheelRodV1.stl
rigParts/rod_smallEnc.stl
rigParts/flexBearingV4.stl
RigParts/mouseWheel/BouncyBearingsV1.stl
rigParts/ExtrudedWheel v2.f3d
rigParts/FlexBearingsAttach.stl
rigParts/LoadCellBase.stl
rigParts/LoadCellWheelConnector.stl
rigParts/archive/ExtrudedWheel v2.f3d
rigParts/archive/FlexBearingsAttach.stl
rigParts/archive/LoadCellWheelConnector.stl
rigParts/archive/MeshBody1.stl
rigParts/archive/baseWheel.stl
rigParts/archive/bounceBearing3.stl
rigParts/archive/flexBearingA.stl
rigParts/archive/flexBearingB.stl
rigParts/archive/loadCellAdapterBottom.stl
rigParts/archive/loadCellAdapterMiddle.stl
rigParts/archive/mouseWheel/BouncyBearingsV1.stl
rigParts/archive/mouseWheel/old/BearingCovers.stl
rigParts/archive/mouseWheel/old/rodWheelV1.stl
rigParts/archive/mouseWheel/wheelRodV1.stl
rigParts/archive/newRod.stl
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

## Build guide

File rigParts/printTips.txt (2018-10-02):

flex bearings:
PETG/ABS/ASA are reccomended, but PLA should be ok.
nozzle 0.4
width 0.4
25% infill
8 top; 8 bottom; 2 shells
3200 mm/min

flex bearings:
PETG/ABS/ASA are reccomended, but PLA should be ok.
nozzle 0.4
width 0.4
25% infill
8 top; 8 bottom; 2 shells
3200 mm/min

12 14.6
28 14.6

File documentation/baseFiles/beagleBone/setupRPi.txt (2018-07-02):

Raspberry Pi setup

Etcher

Create ssh
Create wpa_supplicant.conf containing:

country=US
ctrl_interface=DIR=/var/run/wpa_supplicant GROUP=netdev
update_config=1

network={
    ssid=“Your_SSID"
    scan_ssid=1
    psk=“your_wpaPassword"
    key_mgmt=WPA-PSK
}

sudo apt-get update
sudo apt-get install python-h5py
sudo apt-get install python3-h5py

http://geoffboeing.com/2016/03/scientific-python-raspberry-pi/

sudo apt-get install python-numpy python-matplotlib python-mpltoolkits.basemap python-scipy python-sklearn python-statsmodels python-pandas
sudo apt-get install python3-numpy python3-matplotlib python3-mpltoolkits.basemap python3-scipy python3-sklearn python3-pandas

sudo apt-get install python3-requests python3-pil python3-scrapy python3-geopy python3-shapely python3-pyproj
sudo pip install jupyter geopandas osmnx
sudo pip3 install pygsheets
sudo pip3 install adafruit-io
sudo pip3 install --upgrade pyasn1-modules

download the latest arm linux arduino ide, avoid apt-get
https://www.arduino.cc/download_handler.php?f=/arduino-1.8.5-linuxarm.tar.xz
https://forum.pjrc.com/threads/48825-Installing-Teensyduino-on-Raspberry-Pi-3

sudo ./install.sh
open the ide from the raspberry menu/programming at least once so it can create its librries

tar xf 
or gui

https://www.pjrc.com/teensy/td_download.html
get the installer and the udev rules!
you have to take the udev thing seriously and run
sudo cp 49-teensy.rules /etc/udev/rules.d/

have to make Teensyduinoinstall executable either GUI or
chmod +x TeensyduinoInstall*

add adafruit libraries
https://adafruit.github.io/arduino-board-index/package_adafruit_index.json
add sensor libraries
go to tool/libraries/manage libraries
and search for 
VL6180X
Si7021
SGP30

from the directory

UART ...
https://www.raspberrypi.org/forums/viewtopic.php?t=173461
Serial0
https://electrosome.com/uart-raspberry-pi-python/

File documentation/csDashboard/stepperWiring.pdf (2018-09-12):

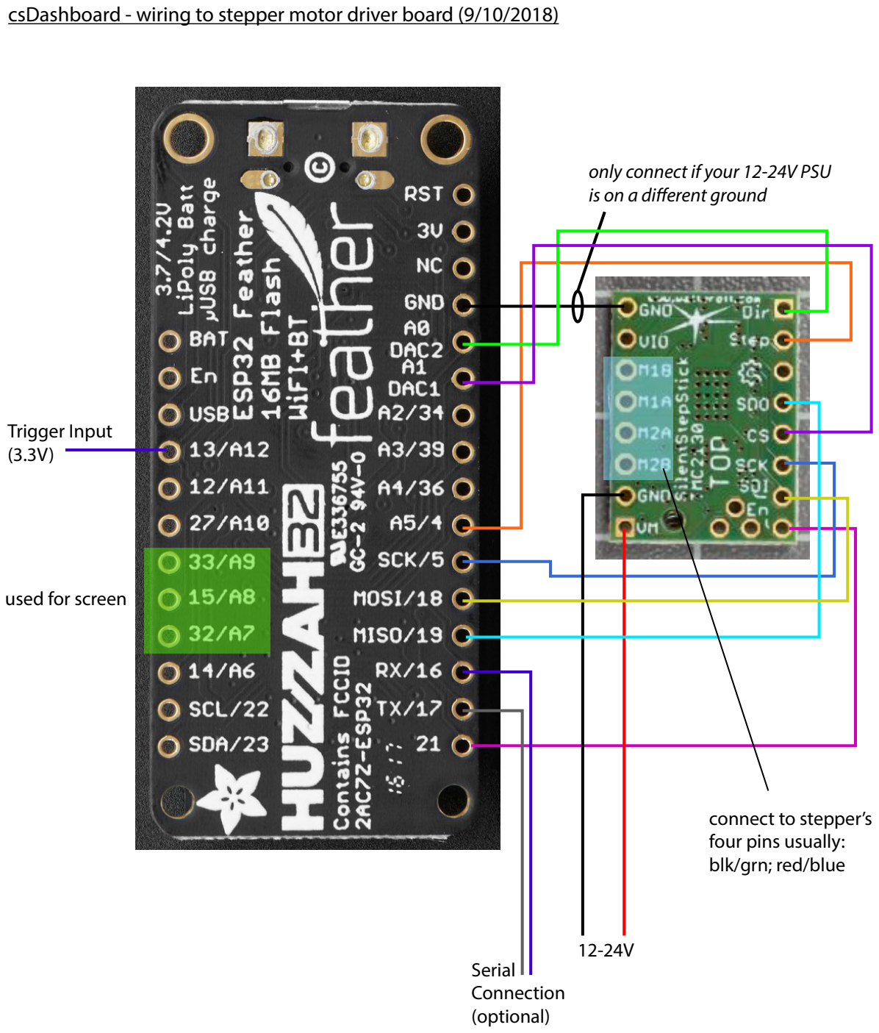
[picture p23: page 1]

used for screen

12-24V

only connect if your 12-24V PSU is on a dierent ground

Serial
Connection
(optional)

Trigger Input
(3.3V)

connect to stepper’s
four pins usually:
blk/grn; red/blue

csDashboard - wiring to stepper motor driver board (9/10/2018)

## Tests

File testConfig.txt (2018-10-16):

[settings]
useGUI = 0
host = abc.com
task = detectionTask

[sesVars]
comPath_teensy = /dev/cu.usbmodem4589150
savePath = /Users/cad/Desktop/cad4/
hashPath = /Users/cad/
shapingTrial = 1
sessionOn = 1
trialNum = 0
curSession = 2
subjID = cad
taskType=detect
totalTrials=6
logMQTT=1
mqttUpDel=0.05
curWeight=20
rigGMTZoneDif=5
volPerRwd=0.0023
waterConsumed=0
consumpTarg=1.5
canQuit = 1
rewardDur = 500
lickAThr = 39000

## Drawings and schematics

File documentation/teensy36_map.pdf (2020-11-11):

### csStateBehavior (v0.99) - Teensy 3.6 Pinout Map

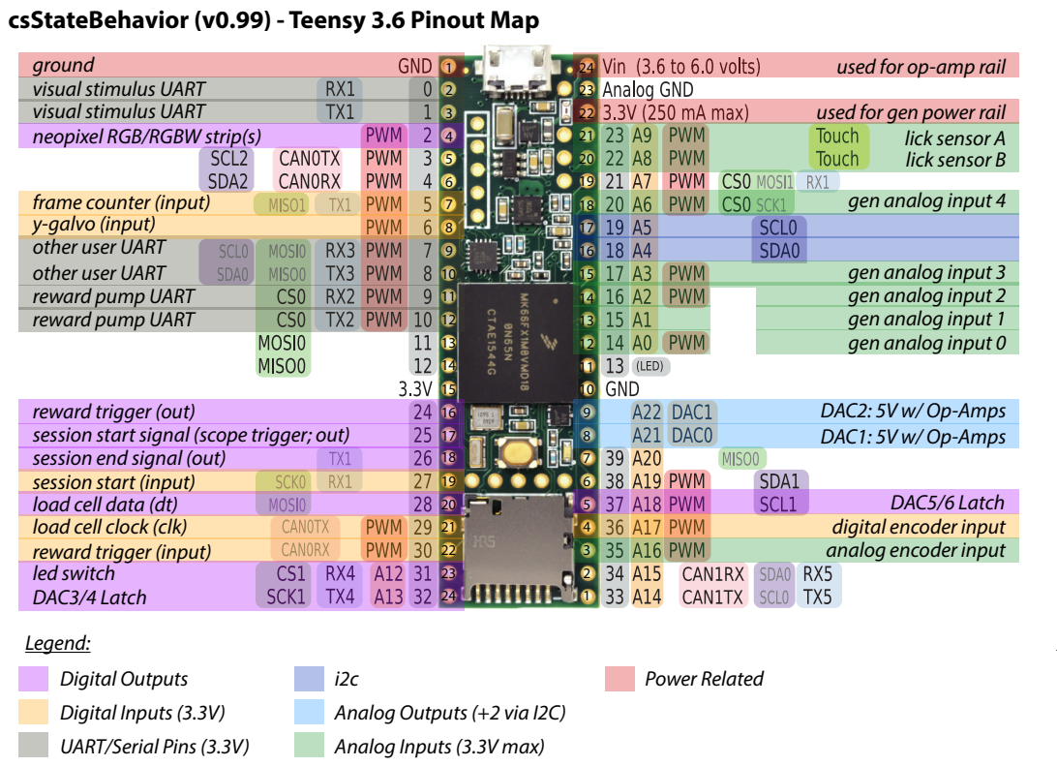
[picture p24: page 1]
DAC2: 5V w/ Op-Amps DAC1: 5V w/ Op-Amps; Power Related

ground
visual stimulus UART
neopixel RGB/RGBW strip(s)

used for op-amp rail
used for gen power rail

lick sensor A
lick sensor B
gen analog input 4

frame counter (input)
y-galvo (input)
other user UART
reward pump UART

gen analog input 3
gen analog input 2
gen analog input 1
gen analog input 0

reward trigger (out)
session start signal (scope trigger; out)
session end signal (out)
session start (input)
load cell data (dt)
load cell clock (clk)
reward trigger (input)
led switch
DAC3/4 Latch
Legend:
Digital Outputs
Digital Inputs (3.3V)
UART/Serial Pins (3.3V)

DAC5/6 Latch
digital encoder input
analog encoder input

Analog Outputs (+2 via I2C)
Analog Inputs (3.3V max)

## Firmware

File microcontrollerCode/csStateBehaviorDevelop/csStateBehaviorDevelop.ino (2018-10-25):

// ~~~~~~~~~~~~~~~~~~~~~~~~~~~~~~~~~~~~~~~~~~~~~~~~~~~~~~~~~~~~~~~~~~~~~~~~~~~~~~~~~~~~~~~~~~~~~~~~~~~~~~
//
// csStateBehavior v0.99 -- 32 bit version (teensy)
//
// Interrupt timed state machine for running behavior tasks and delivering stimuli etc. with a Teensy 3.5/6 board.
// Intended to be used with a python program (csBehavior.py) that enables:
// a) on-demand insturment control
// b) data saving
// c) state-flow logic
//
// By default, csStateBehavior runs at 1KHz.
// It could run at 1.5-2KHz, but I don't reccomend it.
// On a Teensy 3.6, each interrupt takes ~50-200 us depending on how many variables are processed.
//
// Questions: Chris Deister --> cdeister@brown.edu
// Last Update 9/29/2018 --> Added interrupt function to handle flyback-triggered opto stim w/ PMT blanking.
//
//
// ~~~~~~~~~~~~~~~~~~~~~~~~~~~~~~~~~~~~~~~~~~~~~~~~~~~~~~~~~~~~~~~~~~~~~~~~~~~~~~~~~~~~~~~~~~~~~~~~~~~~~~

// ****************************************
// ***** Initialize All The Things ********
// ****************************************
//
// Include config vars
#include "header.h"

// Builtin Libraries
#include <Wire.h>
#include <FlexiTimer2.h>

// Other people's libraries
#include <Adafruit_NeoPixel.h>
#include "HX711.h"
#include <Adafruit_MCP4725.h>


//-----------------------------
// ~~~~~~~ IO Pin Defs ~~~~~~~~
//-----------------------------
//
// a) Analog Input Pins
#define lickPinA  23      // Lick/Touch Sensor A 
#define lickPinB  22      // Lick/Touch Sensor B 
#define genA0 A0
#define genA1 A1
#define genA2 A2
#define genA3 A3
#define analogMotion A16

// b) Digital Input Pins
#define scaleData  29
#define scaleClock  28

// c) Digital Interrupt Input Pins
#define motionPin 36
#define framePin  5
#define yGalvo  6

// d) Digital Output Pins
#define rewardPin 24  // Trigger/signal a reward
#define syncPin 25    // Trigger other things like a microscope and/or camera
#define sessionOver  26
#define rewardMirror 30
#define syncMirror 27
#define ledSwitch 31

#define neoStripPin 2
#define pmtBlank  34


// session header
bool startSession = 0;

uint32_t vStim_xPos = 800;
uint32_t vStim_yPos = 800;

elapsedMillis trialTime;
elapsedMillis stateTime;
elapsedMicros headerTime;
elapsedMicros loopTime;

// e) UARTs (Hardware Serial Lines)
#define visualSerial Serial1 // out to a computer running psychopy
#define dashSerial Serial3 // out to a csDashboard

// f) True 12-bit DACs (I define as an array object to loop later)
// on a teensy 3.2 A14 is the only DAC
// MCP DACs (3&4) can be powered by 5V, and will give 5V out.
// Teensy DACs are 3.3V, but see documentation for simple opamp wiring to get 5V peak.
#define DAC1 A21
#define DAC2 A22

// ~~~ MCP DACs
//Adafruit_MCP4725 dac3;
//Adafruit_MCP4725 dac4;


// **** Make neopixel object
// if rgbw use top line, if rgb use second.
Adafruit_NeoPixel strip = Adafruit_NeoPixel(8, neoStripPin, NEO_GRBW + NEO_KHZ800);
//Adafruit_NeoPixel strip = Adafruit_NeoPixel(30, neoStripPin, NEO_GRB + NEO_KHZ800);
uint32_t maxBrightness = 255;

//--------------------------------
// ~~~~~~~ Variable Block ~~~~~~~~
//--------------------------------

// make a loadcell object and set variables
#define calibration_factor 440000
#define zero_factor 8421804

HX711 scale(scaleData, scaleClock);
uint32_t weightOffset = 0;
float scaleVal = 0;


uint32_t lickSensorAValue = 0;
uint32_t genAnalogInput0 = 0;
uint32_t genAnalogInput1 = 0;
uint32_t genAnalogInput2 = 0;
uint32_t genAnalogInput3 = 0;
uint32_t analogAngle = 0;

uint32_t microTimer;
uint32_t microTimer2;

// a) Set DAC and ADC resolution in bits.
uint32_t adcResolution = 12;
uint32_t dacResolution = 12;

// b) Position Encoder
volatile uint32_t encoderAngle = 0;
volatile uint32_t prev_time = 0;

// c) Frame Counter
volatile uint32_t pulseCount = 0;

// d) Flyback Signal
volatile uint32_t flybackVal = 0;

// e) State Machine (vStates) Interupt Timing
int sampsPerSecond = 1000;
float evalEverySample = 1.0; // number of times to poll the vStates funtion

// e) bidirectional dynamic variables
// ** These are variables you may want to have other devices/programs change
// ** To set each send over serial the header char, the value as an int and the close char '>'
// ** To get each variable ask over serial header char and the close char '<'
// ***** You can add to this, but add a single char header, the default value and increment the knownCount.
// EXAMPLE: To set the state to 2, send "a2>" over serial (no quotes). To get the current state send "a<"
// The following is the legend for each array entry:
// ____ State Machine Related
// a/0: teensyState (the teensy is considered to be the primary in the state heirarchy)
// ____ Reinforcement Related
// r/1: reward duration (if solenoid) or volume (if pump)
// g/2: time out duration (could be used to time a negative tone etc)
// ____ Visual Stim Related
// c/3: contrast of a visual stimulus (python tells teensy and teensy relays to psychopy etc.)
// o/4: orientation of a visual stimulus
// s/5: spatial frequency of a visual stimulus
// f/6: temporal frequency of a visual stimulus
// ____ NEOPIXEL Related (These do not return actual values)
// b/7: brightness of a neopixel strip
// n/8: color of neopixels (1: all white; 2: all red; 3) all green;
// --------> 4) all blue; 5) all purple (the best color) 6) random; 7) pulse rainbows for a bit
// ____ DAC Stim Train Related
// d/9: interpulse duration of train X end the call with the DAC# so d1001 will set the IPI of DAC1 to 100.
// p/10: pulse duration of train X end the call with the DAC# so p101 will set the pulse dur of DAC1 to 10.
// v/11: pulse amplitude of train X end the call with the DAC# so v40001 will set the pulse dur of DAC1 to 4000.
// t/12: stim type of train X end the call with the DAC# 0 is pulse train and 1 is ramp; so t11> will set DAC1 to ramp.
// m/13: max pulses for a stimulus for channel X. m381> will set the number of pulses on DAC1 to 38.
// ____ Misc.
// l/14: current value on loadCell
// z/15: toggle a pin
// q/16: Flyback stim dur (in microseconds)
// e/17: led switch
// x/18: visStim xPos (times 10)
// y/19: visStim yPos
// z/20: visStim size (times 10)


char knownHeaders[] =    {'a', 'r', 'g', 'c', 'o', 's', 'f', 'b', 'n', 'd', 'p', 'v', 't', 'm', 'l', 'z', 'q', 'e', 'x', 'y', 'z'};
uint32_t knownValues[] = { 0,  5, 8000, 0,  0,  4,  2, 1, 0, 90, 10, 0, 0, 0, 0, 0, 100, 1, 2, 0, 10};
int knownCount = 21;



// f) stim trains
// **** here is a map of what each array entry actually does:
// 0: pulse or baseline?
// 1: sample counter to determine how long a train has been in pulse or baseline state
// 2/3: baseline/pulse duration in interrupts (ms by default)
// 4/5: baseline/stim amplitude (as a 12-bit version of 3.3V e.g. 0V is 0 and 3.3V is 4095)
// 6: Stim type (0 for pulse train; 1 for linear ramp) todo: Ramp has a bug I think.
// 7: Write Value (determined by the pulseGen function and is what we write to the DAC each interrupt).
// 8: number of pulses to complete
// todo: swap 7 and 8
uint32_t pulseTrainVars[][9] =
{ {1, 1, knownValues[9], knownValues[10], 0, knownValues[11], knownValues[12], 0, knownValues[13]},
  {1, 1, knownValues[9], knownValues[10], 0, knownValues[11], knownValues[12], 0, knownValues[13]},
  {1, 1, knownValues[9], knownValues[10], 0, knownValues[11], knownValues[12], 0, knownValues[13]},
  {1, 1, knownValues[9], knownValues[10], 0, knownValues[11], knownValues[12], 0, knownValues[13]}
};

uint32_t analogOutVals[] = {pulseTrainVars[0][7], pulseTrainVars[1][7], pulseTrainVars[2][7], pulseTrainVars[3][7]};


// g) Reward Params
uint32_t rewardDelivTypeA = 0; // 0 is solenoid; 1 is syringe pump; 2 is stimulus

// h) Various State Related Things
uint32_t lastState = knownValues[0];  // We keep track of current state "knownValues[0]" and the last state.
uint32_t loopCount = 0; // Count state machine interrupts
uint32_t trigTime = 10; // Duration (in interrupt time) of a sync out trigger.
uint32_t lastBrightness = 10;
bool trigStuff = 0;      // Keeps track of whether we triggered things.

bool blockStateChange = 0;   // Sometimes you want teensy to be able to finish something before python can push it.
bool rewarding = 0;
bool scopeState = 1;
// ***** All states have a header we keep track of whether it fired with an array.
// !!!!!! So, if you add a state, add a header entry and increment stateCount.
int headerStates[] = {0, 0, 0, 0, 0, 0, 0, 0};
int stateCount = 8;

// i) csDashboard
//char knownDashHeaders[] = {'b', 'n','v'};
uint32_t knownDashValues[] = {10, 0, 10};
//int knownDashCount = 3;


void setup() {
  // Start MCP DACs
  //  dac3.begin(dac3Address); //adafruit A0 pulled high
  //  dac4.begin(dac4Address); // sparkfun A0 pulled low

  // todo: Setup Cyclops
  // Start the device

  // neopixels
  strip.begin();
  strip.show();
  strip.setBrightness(100);
  setStrip(2);

  // loadcell
  scale.set_scale(calibration_factor);
  scale.set_offset(zero_factor);
  scale.tare();


  // Analog In/Out
  analogReadResolution(12);
  analogWriteResolution(12);

  // Interrupts
  attachInterrupt(motionPin, rising, RISING);
  attachInterrupt(framePin, frameCount, RISING);
  attachInterrupt(yGalvo, flybackStim_On, FALLING);

  // DIO Pin States
  pinMode(syncPin, OUTPUT);
  digitalWrite(syncPin, LOW);
  pinMode(sessionOver, OUTPUT);
  digitalWrite(sessionOver, LOW);

  pinMode(rewardPin, OUTPUT);
  digitalWrite(rewardPin, LOW);
  pinMode(pmtBlank, OUTPUT);
  digitalWrite(pmtBlank, LOW);
  pinMode(ledSwitch, OUTPUT);
  digitalWrite(ledSwitch, LOW);

  pinMode(syncMirror, INPUT);
  pinMode(rewardMirror, INPUT);

  // Serial Lines
  dashSerial.begin(115200);
  visualSerial.begin(115200);
  Serial.begin(19200);
  delay(20);

  // Start Program Timer
  FlexiTimer2::set(1, evalEverySample / sampsPerSecond, vStates);
  FlexiTimer2::start();
}

void loop() {
  // This is interupt based so nothing here.
}
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

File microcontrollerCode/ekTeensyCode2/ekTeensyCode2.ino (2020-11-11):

// ~~~~~~~~~~~~~~~~~~~~~~~~~~~~~~~~~~~~~~~~~~~~~~~~~~~~~~~~~~~~~~~~~~~~~~~~~~~~~~~~~~~~~~~~~~~~~~~~~~~~~~
// ekMicroController code, modified version of 
// csStateBehavior v0.99 -- 32 bit version (teensy)
// by Chris Deister --> cdeister@brown.edu
// 
// Interrupt timed state machine for running behavior tasks and delivering stimuli etc. with a Teensy 3.5/6 board.
// Intended to be used with a python program (csBehavior.py) that enables:
// a) on-demand insturment control
// b) data saving
// c) state-flow logic
//
// On a Teensy 3.6, each interrupt takes ~50-100 us depending on how many variables are processed.
//
// Changes from Deister version:
//  Removal of unused I/O 
//  Removal of unsused state processes
//  Changed process of pulse-train counting to make it independent of state changes
//  Added next stim time and stim num to process of stim gen to allow for push of stim train timing within 
//    a state and in advance of the trigger time. This allows for independent control of all stimuli within a unchanging state.
// ~~~~~~~~~~~~~~~~~~~~~~~~~~~~~~~~~~~~~~~~~~~~~~~~~~~~~~~~~~~~~~~~~~~~~~~~~~~~~~~~~~~~~~~~~~~~~~~~~~~~~~

// ****************************************
// ***** Initialize All The Things ********
// ****************************************
//

#include <math.h>

// Builtin Libraries
#include <Wire.h>
#include <FlexiTimer2.h>
#include <SPI.h>

// Other people's libraries
// NO #include <Adafruit_NeoPixel.h>
#include "HX711.h"

#include <MCP4922.h>


//-----------------------------
// ~~~~~~~ IO Pin Defs ~~~~~~~~
//-----------------------------
//
// a) Analog Input Pins
// TODO get rid of one of these
#define lickPinA  23      // Lick/Touch Sensor A 
#define lickPinB  22      // Lick/Touch Sensor B 

#define genA0 A0
#define genA1 A1
#define genA2 A2
#define genA3 A3
#define analogMotion A16

// b) Digital Input Pins
#define scaleData  29
#define scaleClock  28

// TODO do we need:
// NO? #define dacGate1 38
// NO? #define dacGate2 39

// c) Digital Interrupt Input Pins
// NO #define motionPin 36
#define framePin  5
#define yGalvo  6

// d) Digital Output Pins
#define rewardPin 24  // Trigger/signal a reward
#define syncPin 25    // Trigger other things like a microscope and/or camera

// TODO decide if useful
#define sessionOver  26
#define rewardMirror 30

// TODO decide if we want TTL triggering #define syncMirror 27 removed all traces of LED swtich and other removed
// NO #define ledSwitch 31

// NO #define neoStripPin 2
// NO #define pmtBlank  34


// session header
bool startSession = 0;  // TODO this is only used for the end session, if we don't need -> delete

// NO uint32_t vStim_xPos = 800;
// NO uint32_t vStim_yPos = 800;

// TODO delete these if not needed

elapsedMillis trialTime;
elapsedMillis stateTime;
elapsedMicros headerTime;
elapsedMicros loopTime;

// TODO this is hard coded into the Stim Gen, change back
uint32_t dacNum = 5;


// NO e) UARTs (Hardware Serial Lines)
// NO #define visualSerial Serial1 // out to a computer running psychopy
// NO #define dashSerial Serial3 // out to a csDashboard

// f) True 12-bit DACs (I define as an array object to loop later)
// on a teensy 3.2 A14 is the only DAC
// MCP DACs (3&4) can be powered by 5V, and will give 5V out.
// Teensy DACs are 3.3V, but see documentation for simple opamp wiring to get 5V peak.
#define DAC1 A21
#define DAC2 A22

// ~~~ MCP DACs

// TODO Change LDAC pin (see readme) if appropriate
MCP4922 mDAC1(11, 13, 33, 37);
MCP4922 mDAC2(11, 13, 34, 32);

// NO  **** Make neopixel object
// NO if rgbw use top line, if rgb use second.
// NO Adafruit_NeoPixel strip = Adafruit_NeoPixel(8, neoStripPin, NEO_GRBW + NEO_KHZ800);
// NO Adafruit_NeoPixel strip = Adafruit_NeoPixel(30, neoStripPin, NEO_GRB + NEO_KHZ800);
// NO uint32_t maxBrightness = 255;

//--------------------------------
// ~~~~~~~ Variable Block ~~~~~~~~
//--------------------------------

// make a loadcell object and set variables
#define calibration_factor 440000
#define zero_factor 8421804

HX711 scale(scaleData, scaleClock);
uint32_t weightOffset = 0;
float scaleVal = 0;

// NO bool sDacGate1 = 0;
// NO bool sDacGate2 = 0;

uint32_t lickSensorAValue = 0;
uint32_t genAnalogInput0 = 0;
uint32_t genAnalogInput1 = 0;
uint32_t genAnalogInput2 = 0;
uint32_t genAnalogInput3 = 0;
uint32_t analogAngle = 0;

// TODO These might be for something?
// uint32_t microTimer;
// uint32_t microTimer2;

// a) Set DAC and ADC resolution in bits.
uint32_t adcResolution = 12;
uint32_t dacResolution = 12;

// b) Position Encoder
volatile uint32_t encoderAngle = 0;
volatile uint32_t prev_time = 0;

// c) Frame Counter
volatile uint32_t pulseCount = 0;

// d) Flyback Signal
volatile uint32_t flybackVal = 0;

volatile uint32_t lineTime = 0;
volatile uint32_t curLine = 0;
volatile uint32_t lastLine = 0;

// e) State Machine (vStates) Interupt Timing
int sampsPerSecond = 1000;
float evalEverySample = 1.0; // number of times to poll the vStates funtion
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

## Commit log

2018-06-21 made mount screwholes countersunk a tad
    [mainMount.stl]
2018-06-29 0.2 -- More Parts Start csVisual Move
    [BearingCovers.stl, BouncyBearingsV1.stl, MA3-X-125-B.SLDPRT, bearingWSlot.stl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]
2018-07-03 prelim teensy changes for eric
2018-08-03 v0.8 -- Integration and Performance
    a) Packaged csPiCam.py in "CameraStuff" This is a simple python3 program that runs on a raspberry pi and allows csVisual to trigger a raspberrypi camera (GPIO11; 6th one down on the left). The video 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
    b) Added a draft Jupyter notebook called "h264OpenCVHDF5.ipynb" that uses OpenCV to read frames and timestamps from h264s produced by csPiCam. Also, it can parse the HDF files produced from csVisual.
    c) Added a psychopy script "csGabor.py" to play a gabor with paramaters that can be updated rapidly over serial. It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
    [BearingCovers.stl, BouncyBearingsV1.stl, MA3-X-125-B.SLDPRT, basicSetup.fzz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]
2018-08-05 v0.85 -- Significant Teensy Script Changes
    * Stim Generation Related
    a) DAC stim gen totally reworked.
    b) Key stim gen variables in the arrays reset in each state's header.
    c) Ramp bug is fixed (wasn't actually there)
    d) Stim gen arrays track each pulse or ramp now, allowing you to logically toggle them on and off in each state.
    e) Two functions can be called "stimTrainsStimState()" and "stimTrainsNoStimState()"
    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
2018-08-06 v0.9
    v0.9
    *** You need to update adafruit-io python library to the latest, and the ESP32 libraray to the latest too.
    ~~~~Python Changes
    * csVisual.py
    a) Adafruit IO is now enforcing username and key as a pair to create a client object. I have changed the creator function to read a text file the has two lines with the first being the user name and 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
    b) hdf filename is timestamped
    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
2018-08-06 v0.91 -- Load Cell Improvements
    Completley overhauled how loadcells are dealt across the stack. The GUI allows for offsets to be set and the hx711 amp is now fixed to work with a teensy thanks to this tip from Github user igorjanse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
2018-08-08 v0.92 - More device control in csVisual crippled csDashboard
    a) I've expanded the adhoc device control in python, and laid out a preliminary GUI design.
    b) csDashboard in more functional, but the screen aspect is broken at this point. For now, csDashboard is mostly a relay for stepper control. I'm in the midst of overhaulling the serial communication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
2018-08-08 v0.921 -- Subtle Folder Reorg
    Added some rig parts (load cell) and moved an archive folder.
    [loadCellAdapterBottom.stl, loadCellAdapterMain.stl, loadCellAdapterMiddle.stl]
2018-08-16 v0.96 -- csDashboard Improvements
    Syringe pump based rewards are fully configurable via csDashboard. Screen works, serial/tcp do not (yet).
2018-09-17 fixed some errors in stepper calculations
2018-09-19 v0.985 -- Quad DAC
    * Added two extra MCP-based DAC lines on the Teensy
    * Teensy streams genAnalog0-3 by default now.
    * Currently Dac3 and Dac4 mirror Dac1 and Dac2 respectivley.
2018-09-25 v0.987 -- Manual Merge of csBehavior.ino
    Will be changing name of teensy script to csTeensyBehavior
2018-09-26 v0.988 -- Update Analog Out
    Analog output handline is overhauled. Now, only five serial variables are used to control paramaters of all four DAC lines. Documentation mostly reflects these changes.
    [ExtrudedWheel v2.f3d, FlexBearings.stl, FlexBearingsAttach.stl, LoadCellBase.stl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]
2018-10-02 v0.989 - Reorg on documentation
    Added provisional flyback opto documentation.
    [basicSetup.fzz]
2018-10-02 Miller Effect warning in flyback opto documentation.
2018-10-08 some merging
    [rodV2.stl]
2018-10-16 prelim device detection
    added a function in the GUI class that polls the dev folder to look all possible serial devices
    checkForDevicesUnix(someFilterString)
2018-10-22 v0.99 -- Better Visual Stim Control
    Main Changes:
    a) csGabor.py parses all of the visual stimulus packet
    b) csStateBehavior.ino sends size of stimulus now too.
    c) fixed some general bugs.
    Other Changes:
    Added some shell scripts to help set up a raspberry pi for running the task, and or giving visual stimuli.
    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
2018-10-23 Major Changes in Trial Variable Handling
    Big overhaul in how trial-by-trial variables are handled.
    All are specified in csVars using a catagortical dictionary and enumerating probabilities within those dictionaries.
    In task, the variable dicts are looped over. Three main dicts: timing, sens, and optical
    csParser will have to be overhauled as the attributes are now automatically generated and are different.
    Also, I added a concept of local python time. Python was always keeping track of the teensy clock, as streamed over serial. But now, there are some local variables that are copies of that clock. I ha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
2018-10-25 better encapsulation of trial variables
    Effecticvley everything about trial variables is encapsulated in the csVars class.
    Added a function in csVars that allows for generating/regenerating variables on the fly (easily).
    Got rid of the extra variable label dictionaries, and now have a key in the dicts whose value is the list.
    Overall everything is much more efficient
    I need to farm out the visual serial call, just like the analog updates.
    [LoadCellBase.stl]
2018-10-28 csGUI class changes
    a) The parent window is now made from a seperate function. I have removed it from __init__
    [mainSyringeHolder.stl, motorMountNema17.stl, motorMountNema17_v1.f3d, syringeClamp.stl]
2018-11-05 parent gui changes
    50%, but functional again
    [testRod3.stl]
2018-11-06 more on linux load
    [rod44.stl, rodV4.stl, rodV41.stl, rodV42.stl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]
2018-11-07 simplified and fixed dictionary import/save issues
    only thing that remains is that parent window's text variables aren't updating
    [Body1.stl, rod45.stl, rod46.stl, rod47.stl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]
2018-11-07 v1.0
    Merging all variable handling fixes to main branch.
    [Body1.stl, LoadCellWheelConnector.stl, MeshBody1.stl, rod44.stl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]
2018-11-07 cleaned up debuging prints and added example dicts
    [opticalVars.csv, sensVars.csv, sesVars.csv, timingVars.csv]
2018-11-10 mostly changes to rig parts
    [FlexBearingV2.f3d, FlexBearingV21.stl, encoderHolder2.stl, encoderMount_v21.f3d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]
2018-11-10 important dictionary indexing changes
    In some cases, I was asssuming the order in the dictionary was deterministic. Menaing that if I made a dictionary as vars={'a':1,'b':2,'c':3} then if you call for x in list ... then x would go a,b an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
    Now when trialVars are computed, they generate a list of computed numbers and an index. The index is just an ordered list of the key's in order of their processing. When they are used later, the inde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
2018-11-11 v1.01
    Big changes to prob calculation. Faster and easier to read. I use shuffle instead of the multi-array mapping I was doing.
    Also, trial variables stay as a pandas frame, it gets saved out too.
2018-11-12 v1.05 -- Added MQTT Inspection/Backup
    There is now an MQTT window that can be invoked from the parent window. This window lets you connect to the MQTT server and look at a list of all available feeds. You can select a feed and inspect th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
    [sp_sixInchBase.stl]
2018-11-12 minor mqtt additions
    [flexMount2v4.stl]
2018-11-16 notes saving in attributes is buggy, but won't crash
    [flexMount_v23.stl]
2018-11-23 v1.06 - Abstracted Most Task Code
    The infrastructure to make most task code common/reuseable for all tasks
    [rod_largeEnc.stl, rod_smallEnc.stl, testWall.stl]
2018-12-03 v1.096 -- updated teensy map, settled on SPI write functions
2019-01-07 v1.1
    * some water consumption changes in python code
    * added/changed some python documentation notebooks
    * fixed teensy map to show galvo pins
    * made pulse counting ubiquitous for all dacs, each pulse type can still, and needs to, have some code to listen to the pulse counter or not.
2019-02-11 subtle change to teensy pulse counting
2019-02-11 reverted teensy back to check pulses in s8 too
